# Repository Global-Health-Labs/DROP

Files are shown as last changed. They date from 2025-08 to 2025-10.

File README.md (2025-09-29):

# DROP Project Overview
DROP is a comprehensive automated diagnostic assay development platform developed by Global Health Labs. It's designed to accelerate and optimize the development of diagnostic tests, specifically focusing on:

- Lateral Flow Assays (LFAs) - rapid diagnostic tests like pregnancy tests or COVID antigen tests
- Nucleic Acid Amplification Tests (NAATs) - molecular tests like PCR, LAMP, and RPA

# Development Benefits

- Accelerated Timelines: Reduces development time and hands-on work
- Improved Scalability: Enables large-scale experiments
- Enhanced Reproducibility: Minimizes human variability
- Cost Effective: Reduces resource requirements for assay optimization

# Key Components
1. Hardware Platform

- Built around a Hamilton STAR liquid handling robot
- Custom 3D-printed LFA strip and cassette holders
- Integrated camera system for automated imaging
- Specialized deck layouts for different assay types
- HEPA filtration and UV sterilization for NAAT applications

2. Software Ecosystem

**RADA (Robotic Assay Development Application)**

- AWS-based web application that simplifies robot operation
- Generates worklist files (CSV instructions for the robot)
- Features separate interfaces for LFA and NAAT experiments
- Includes admin capabilities for managing users, deck layouts, and liquid classes
- Built with user-friendly interface to reduce technical barriers

**Image Analysis Software**

- Python-based LFA image analysis tools (LFA_image_analysis)
- Automated analysis of test and control lines
- Signal-to-noise ratio calculations
- Flexible parameters for different LFA formats

**Supporting Tools**

- Robot worklist generators
- Thermocycler analysis software
- Documentation system (MkDocs-based)

3. Protocols and Methods

- Standardized workflows for both LFA and NAAT development
- Design of Experiments (DoE) approaches
- Validation procedures and troubleshooting guides

# Applications
The DROP system has been used for:

**LFA Applications:**

- Antibody pair screening and optimization
- Membrane material optimization
- Buffer condition optimization
- Conjugate chemistry development
- Drying and spraying condition optimization

**NAAT Applications:**

- PCR optimization
- LAMP (Loop-mediated Isothermal Amplification) development
- RPA (Recombinase Polymerase Amplification) optimization
- Primer design and validation

# Current State

- Complete hardware and software designs are available on GitHub
RADA web application is deployment-ready
- Comprehensive documentation and troubleshooting guides included
- Proven track record in accelerating diagnostic development

This is a sophisticated, production-ready platform for automated diagnostic assay development that combines robotics, custom software, and validated protocols to streamline the traditionally manual and time-intensive process of diagnostic test optimization.

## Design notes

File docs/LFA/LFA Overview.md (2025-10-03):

Lateral Flow Assays (LFAs) are a popular diagnostic technology that enables sophisticated protein based chemistries to be run at or near the point of care. With low cost and ease of use, LFAs have been used for applications that span across a wide range of targets. These targets include bacteria, viruses, toxins, and more. Even though the use of these tests is fairly straightforward, there can be a significant investment required to create high performance LFAs. 

An example of a traditional LFA is shown in Figure 1 below. This is an example of a direct immunoassay, where a capture antibody is immobilized on the test membrane that is specific to the analyte of interest. A control antibody is immobilized on a second line to verify that the test results can be interpreted correctly. Antibodies conjugated to a label, often a gold or latex nanoparticle, are dried into a conjugate pad placed upstream from the test membrane. Before the conjugate pad, a sample pad is placed onto which the sample and/or running buffers are placed when the LFA is run. Downstream from the test membrane is a wicking pad, which helps to drive fluid flow through the test membrane. 

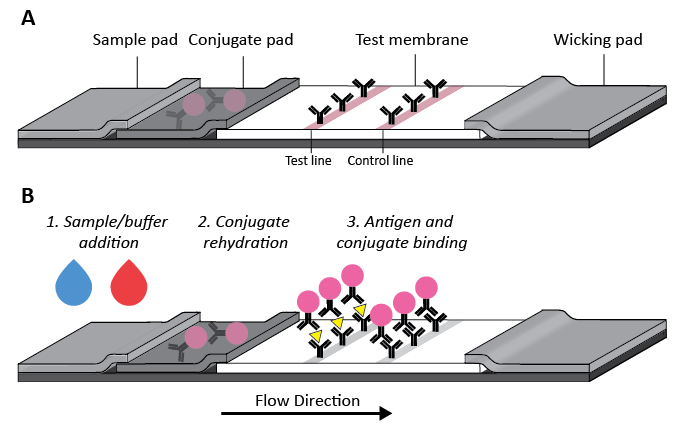
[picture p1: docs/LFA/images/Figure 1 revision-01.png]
LFA Background
 <br>
<small>Figure 1. Schematic of a classic LFA, from https://doi.org/10.1007/s00216-022-03897-9. The image depicts the materials involved in an LFA, which often includes a sample pad, a conjugate pad, a test membrane onto which a test and control ine are striped, and a wicking pad to drive flow (A). Typical use involves the addition of a sample and/or buffer to the sample pad, which flows downstream to rehydrate the conjugate dried into the conjugate pad (B). Liquid then moves into the test membrane onto which a test and/or control line will appear depending on whether analyte is present in the sample. All remaining liquid and unbound proteins then flow into the wicking pad. </small>

While an LFA is designed to be an quick and easy to use diagnostic, there are a lot of components that go into the optimization process. This includes, but is not limited to: 

1. Materials choice and dimensions: sample pad, conjugate pad, test membrane, wicking pad, and backing card
2. Material treatment: blocking, prewetting, etc
3. Assay format: direct, competitive, streptavidin test line with biotinylated capture antibody, etc
4. Molecular recognition element(s): antibody or antibody fragment, aptamer, proteins generated through directed evolution, computational, or rational design
5. Conjugation chemistries
6. Striping, spraying, and drying conditions 
7. Running buffer components 
8. Assay timing 

To address the time and monetary cost involved in LFA research and development, GH Labs developed a platform utilizing an automated liquid handling system. This system, termed RoboLFA, is a subcategory of the DROP platform. RoboLFA consists of LFA specific hardware, software, and protocols to enable large optimization or characterization expriments with limited hands-on time required. The system is described in detail in a paper by Anderson et al<sup>[1](https://link.springer.com/article/10.1007/s00216-022-03897-9)</sup>. Two applications using the roboLFA system are discussed in papers by Cate et al<sup>[2](https://pubs.acs.org/doi/10.1021/acsomega.1c01253)</sup> and Cantera et al<sup>[3](https://pmc.ncbi.nlm.nih.gov/articles/PMC8340086/)</sup>. Additional information on how to implement and/or modify this system is found in the respective sections for Hardware, Software, Protocols, and Example Efforts. 

## References
<small>
[1] Anderson, C.E., Huynh, T., Gasperino, D.J. et al. Automated liquid handling robot for rapid lateral flow assay development. Anal Bioanal Chem 414, 2607–2618 (2022). https://doi.org/10.1007/s00216-022-03897-9 <br>
[2] Cate, D. M., Bishop, J. D., Hsieh, H. V., et al. Antibody Screening Results for Anti-Nucleocapsid Antibodies Toward the Development of a Lateral Flow Assay to Detect SARS-CoV-2 Nucleocapsid Protein. ACS Omega 2021 6 (39), 25116-25123. DOI: 10.1021/acsomega.1c01253 <br> 
[3] Cantera, J. L., Cate, D. M., Golden, A., et al. Screening Antibodies Raised against the Spike Glycoprotein of SARS-CoV-2 to Support the Development of Rapid Antigen Assays. ACS Omega 2021 6 (31), 20139-20148. DOI: 10.1021/acsomega.1c01321 <br> </small>

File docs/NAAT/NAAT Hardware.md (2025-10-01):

Custom hardware is not required to run NAAT assays, as the Hamilton STAR system is already equipped to handle both tube- and plate-based workflows. For enhanced flexibility, we’ve included CAD files below that allow for the modification of commercially available cooling blocks to accommodate 0.5–2 mL tubes. These modified blocks are compatible with the Hamilton cooling deck, enabling efficient temperature control without the need for proprietary components.

:simple-opensourcehardware: - [CAD Files](https://github.com/Global-Health-Labs/DROP/tree/main/hw)

**Table 1.** Modifications to heating/cooling blocks to enable alignment on cooling deck. 

| No.| File Name       | Description    | Vendor            | Part No. | Qty  | Modified | Link  |
| :--| :-------------- | :------------- | :---------------- | :------- | :--: |:-------- |:-----: |
| 1  | 047295.SLDPRT  | 2 mL tube holder block| NA        | NA      | 1    |Holes for alignment posts| Hamilton #188035|
| 2  | 047296.SLDPRT  | 0.5 mL tube holder block | NA     | NA      | 1    |Holes for alignment posts| Hamilton #188035|

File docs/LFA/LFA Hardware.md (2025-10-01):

LFAs can come in many different forms. We have developed holders to address two of the most commonly used formats, a strip and a cassette. Other form factors can be integrated, but may require additional development to get a holder that is compatible with both the form factor of the LFA and the form factor of the deck postiions on the Hamilton STAR. These holders may also be adapted to other liquid handling systems. 

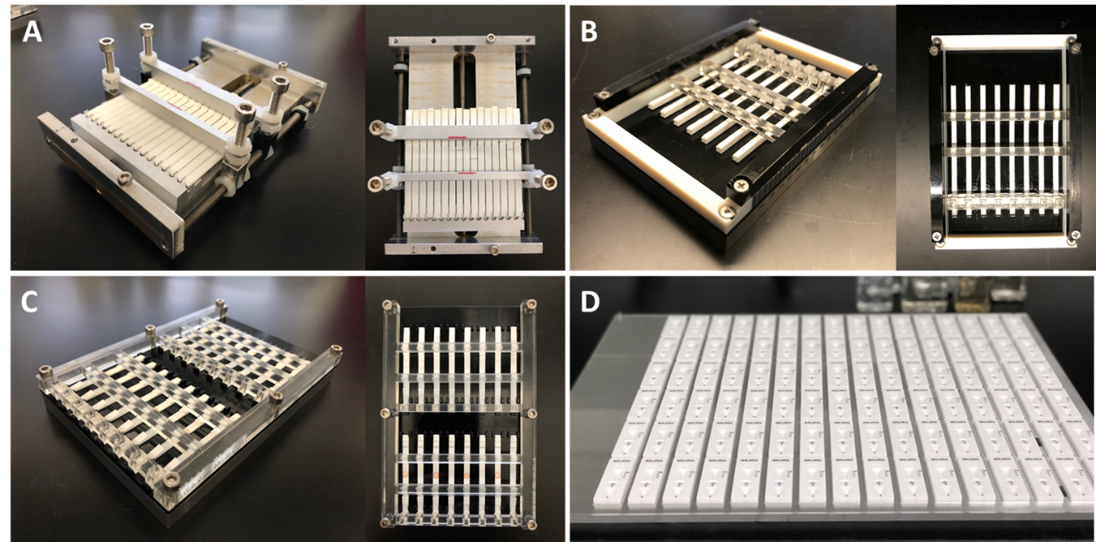
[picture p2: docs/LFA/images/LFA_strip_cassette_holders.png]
LFA Strip Holders
 <br>
<small>Figure 1. Image of the developed LFA strip (A), (B), and (C), and cassettes (D) from https://doi.org/10.1007/s00216-022-03897-9</small>

The objective of this document is to describe the pieces of hardware that might be required to operate the DROP system. This includes modifications to the base assembly from Hamilton, machined aluminum trays, laser cut acrylic sheets and 3D printed strip holders. This document has been prepared such that the entire assembly can be understood, as many parts relate to one another in the final deck layout.  

:simple-opensourcehardware: - [CAD Files](https://github.com/Global-Health-Labs/DROP/tree/main/hw)

### Custom Deck Modifications

The CAD files required for the custom deck modifications are broken into individual assemblies. These modifications assume that the carrier is an older version of the Hamilton Carrier. Newer version of the Hamilton Carrier are plastic and have slightly different dimensions. Additional development to add the alignment posts would be required if using a newer Hamilton Carrier for LFA applications. 

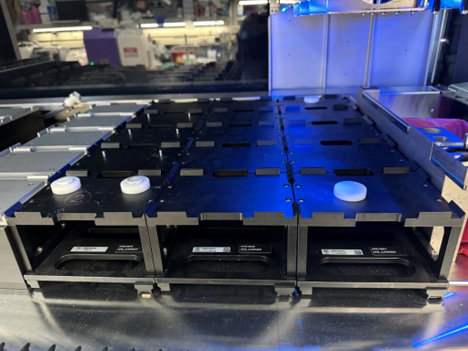
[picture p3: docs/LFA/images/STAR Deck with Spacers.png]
Hamilton Deck Modifications
 <br>
<small>Figure 2. Hamilton base carriers that have pegs and spacers added in their desired locations.  Associated parts are described in Tables 1 and 2.</small>

**Table 1.** Assembly of Hamilton base carriers that are modified so they can provide fiducial markers when LFA or cassette holders are placed on top. 

| No.| File Name       | Description    | Vendor             | Qty   | Modified | Link |
| :- | :-------------- | :------------- | :----------------  | :--: |:-------- |:---: |
| 1  | 047284.SLDASM   | Base assembly  | Hamilton Robotics  | 3     |          |      |
| 2  | 047283.SLDPRT   | Carrier base   | Hamilton Robotics 188039/00 | 1     |          | 1    |
| 3  | 047279.SLDASM   | Hamilton stand | Hamilton Robotics  | 3     |          | 1    |
| 4  | 047274.SLDPRT   | Top plate      | Hamilton Robotics  | 3     | Pin holes added | 3 |
| 5  | 047275.SLDPRT   | Leg            | Hamilton Robotics  | 2     | No       | 3    |
| 6  | 047281.SLDASM   | Hamilton stand | Hamilton Robotics  | 1     |          | 1    |
| 7  | 047273.SLDPRT   | Top plate      | Hamilton Robotics  | 1     | Pin and threaded holes added| 6 |
| 8  | 047275.SLDPRT   | Leg            | Hamilton Robotics  | 2     | No       | 6    |
| 9  | 047282.SLDASM   | Hamilton stand | Hamilton Robotics  | 1     | No       | 1    |
| 10 | 047277.SLDPRT   | Top plate      | Hamilton Robotics  | 1     | No       | 9    |

**Table 2.** Alignment posts and spacers to enable correct assembly. 

| No.| File Name       | Description    | Vendor            | Qty  | Modified | Link  |
| :- | :-------------- | :------------- | :---------------- | :--: |:-------- |:-----: |
| 11 | 047288.SLDPRT   | Alignment posts| Custom            | 2    |          | 1 + 16 |
| 12 | Hamilton_spacer.SLDPRT | Spacer with top hat | Custom| 2    |          | 1 + 16 |
| 13 | Hamilton_spacer_2.SLDPRT | Flat spacer | Custom        | 2    |          | 1 + 16 |

Note: Hamilton_spacer.SLDPRT doesn’t correctly account for tolerances, there is a need for us to improve the file to account for tolerances if this part is 3D printed.

### RoboLFA Strip Holder 
An LFA strip holder is helpful when a cassette has not yet been designed or the LFA dimensions are still requiring adjustment. Some LFAs on the market are in strip form, such as *Milenia Biotec HybriDetect Universal Lateral Flow Assays* and over-the-counter HCG tests, and therefore would stay in this category throught the entire research and development lifecycle. On this site we will mostly discuss our most commonly used strip holder, which consists of the following:

- Aluminium plate (85.5 x 127.8 mm) with six holes compatible with (#6-32) screws  
- 3D printed base plate designed to fit the width and length of the LFA strips
- 3D printed top plate designed with necessary pinch points, wells for reagent addition, and read window   
- 6 Screws (6/32 x 1/2")

When starting a new RoboLFA effort, it is critical to understand the requirements for a strip holder. This includes the length and width of the strip, the location and thickness of pinch points, the location and volume required for reagent addition, and the location and size of the read window. Each of these factors can be modified in the CAD files linked below. More detailed instructions can be found [here](./LFA%20Protocols.md). 

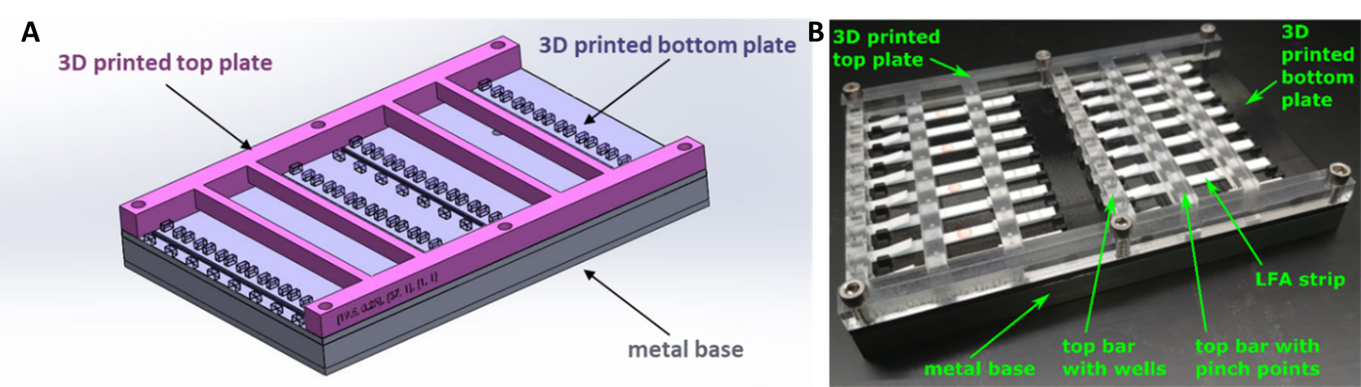
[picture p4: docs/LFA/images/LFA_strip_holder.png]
LFA Strip Holders
 <br>
<small>Figure 2. Strip holder to hold non-cassetted LFAs. The designed holder consists of three parts, (1) an aluminum base plate, (2) 3D brinted base plate and (3) 3D printed top plate. The bottom plate is designed with guide posts for consistent placement of a strip, while the top plate is designed to have pinch points and wells where required. Image from https://doi.org/10.1007/s00216-022-03897-9</small>

**Table 3.** LFA Strip Holder which consist of an aluminum base onto which 3D printed pieces are screwed. Similar to the RoboLFA Cassette Holder, The size and spacing of the strips can be varied depending on the need of the specific LFA. The dimensions of the wells, pinch points, and read windows can all be modified as needed. We typically have used ABS (acrylonitrile butadiene styrene) for this part.

| No.| File Name       | Description    | Vendor            | Qty  | Modified | Link  |
| :- | :-------------- | :------------- | :---------------- | :--: |:-------- |:-----: |
| 14 | 047286.SLDPRT   | LFA strip holder base | Custom            | 1-5  |          | 1 |
| 15 | 056923.SLDPRT (LFA Holder 3)| LFA strip top+bottom frame|Custom| 1-5  |          | 14|

We have two other versions of the strip holder that have some usability issues that need to be addressed. The other two strip holders are either challenging to set up reproducibly or require additional engineering on the clamping mechanism. More details about both of these holders can be found in the [supplemental material](https://doi.org/10.1007/s00216-022-03897-9). 
If we were to get additional time to further improve the strip holders, the most promising holder is the lego inspired assembly that allows for different 3D printed cross bars to be added interchangeably in 0.5mm increments along the length of the holder. This design allows for the manual adjustment of holder components (wells, pinch points, etc) without the need to manufacture additional parts.

### RoboLFA Cassette Holder
An LFA cassette holder is used when the strip dimensions have been locked and is further along the R&D pipeline. The cassette holder has defined spacing, allowing for precise liquid delivery and imaging across a large number of LFA devices.  

The cassette holder consists of:  

+ A 1/4" aluminum plate (40 x 48 cm) with the following modifications  
    - Two pins to guide the acrylic sheet in place  
    - Two drilled holes (dimensions) that enable consistent placement of the cassette holder onto the Hamilton Deck  
+ A 1/16" acrylic sheet (40 x 48 cm) with the following modifications
    - Laser cut to fit the cassette dimensions (example CAD files fit 80 and 96 cassettes respectively)
    - Two pin holes to guide on the aluminum plate 

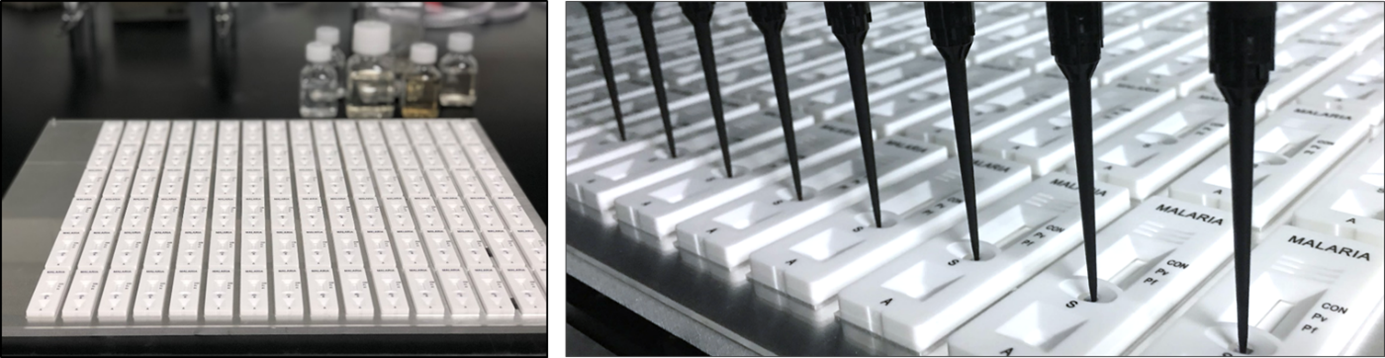
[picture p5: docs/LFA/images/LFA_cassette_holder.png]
LFA Cassette Holders
 <br>
<small>Figure 3. Holder for cassetted LFAs. The designed holder consists of two parts, (1) an aluminum base plate, (2) a laser cut 1/16" acrylic sheet designed to fit cassettes with little "wiggle room".  Image from https://doi.org/10.1007/s00216-022-03897-9</small>

| No.| File Name       | Description    | Vendor             | Qty  | Modified | Link  |
| :- | :-------------- | :------------- | :---------------- | :--: |:-------- |:-----: |
| 16 | 047287.SLDPRT   | LFA cassette deck| Custom            | 1    |Holes for alignment posts and posts for cassette holder| 12 + 13 |
| 17 | 038379_v1.SLDPRT or  038379_v2.SLDPRT (LFA Holder 4) | LFA cassette holder | Custom            | 1    |Holes for posts and cassettes (LFA cassette dependent)| 16 |

## Deck build 

The hardware above is placed onto the deck in the following, respective manners, for the cassette and strip holders. 

Deck Layout with cassette holder <br>
<small>Figure 4. Deck layout with cassette holder and corresponding guidance spacers. </small>

Images of deck build with both the LFA strip holder 

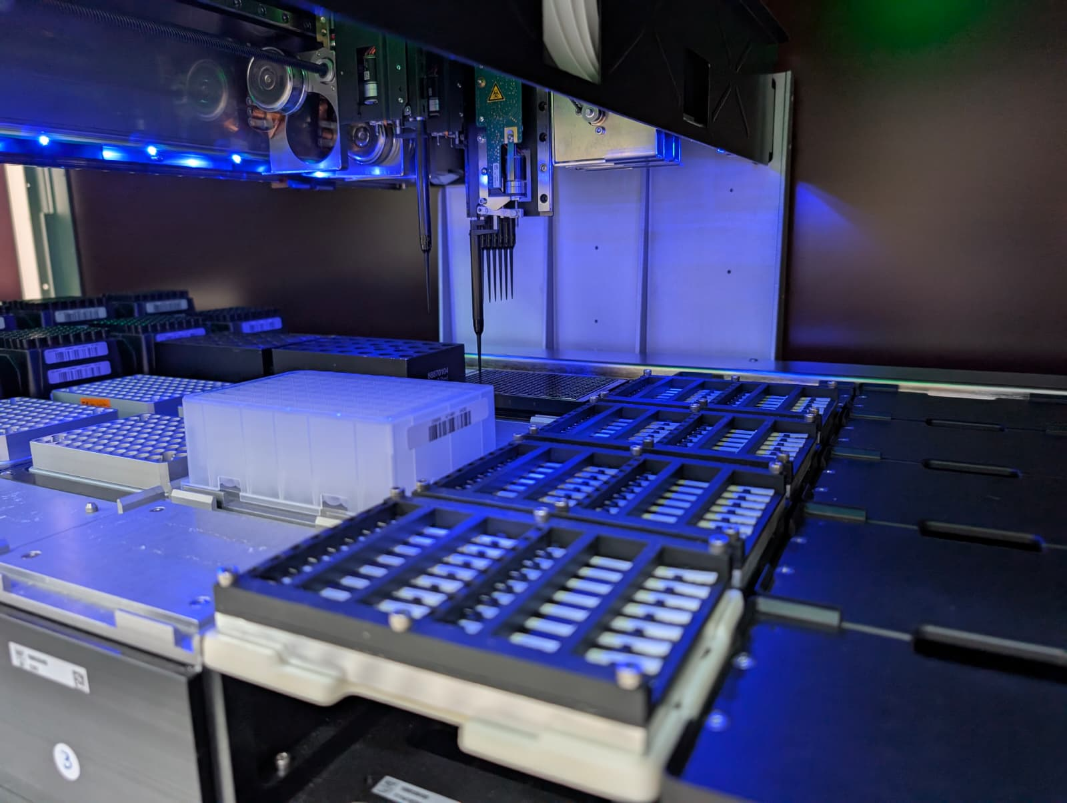
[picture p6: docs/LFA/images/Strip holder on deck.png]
Deck Layout with LFA strip holder
 <br>
<small>Figure 5. Deck layout with strip holder. </small>

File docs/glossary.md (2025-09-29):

## Definitions

There is a lot of jargon associated with the DROP system. The definitions are grouped into sections based on the time of need, including general use, working with worklists, etc. 

## Abbreviations
| Term             | Definition                          |
| :--------------- | :----------------------------------- |
| `NAAT`           | Nucleic Acid Amplification Test |
| `LFA`            | Lateral Flow Assay |
| `DROP`           | Diagostic Robotic Optimization Platform |
| `AWS`            | Amazon Web Services|
| `RADA`           | Robotic Assay Development Application |
| `RPA`            | Recombinase Polymerase Amplification |
| `LAMP`           | Loop-mediated Isothermal Amplification |
| `PCR`            | Polymerase Chain Reaction |
| `DW`             | Deep well plates | 
| `NTR`            | Nesting tip racks | 
| `RDT`            | Rapid diagnsotic test |

## General definitions 
| Term                     | Definition                          |
| :----------------------- | :----------------------------------- |
| `worklist`        | The worklist is a .csv file that is input into the Hamilton Run Control to the robot what actions to follow and in what order. The file containing the worklist must end with ‘worklist.csv’ otherwise the Hamilton software will not recognize it. The file containing the worklist must end with worklist.csv; otherwise, the Hamilton software will not recognize it. The file must be a plain .csv file (not a UTF-8 or any other csv version). A worklist can be made manually or by coding. For LFA optimization work, we have python-based code called the “Robot Worklist Generator”. The worklist is composed of 21 columns (two of which are optional) and infinite rows. The identity and definition of each of these columns is described in Section 8. The order of the columns does not matter.  |
| `Method`          | A Hamilton specific piece of software that has been designed to carry out an experiment. Methods can be simple (always pipette a known volume between known locations) or complex (insert a .csv file with a range of different commands that can pipette any volume within reason between any location available on the deck). |
| `Deck`            | The area on the robot where things happen. It includes where the pipette tips are stored, where plates can be placed, and even includes the waste area. |
| `Stock plate(s)`  | Plates that have all stock reagents required for the experiment. Typically, we can use the stock plates as the location to prepare and mix the mastermix as well. |
| `Assay plate(s)`  | Plates where the mastermix and sample (or just template) are added. We have spots on the deck for both 96 well and 384 well PCR plates. A flat bottom plate can also be used as an "assay plate", depending on the application.|
| `Liquid Class(es)`| A liquid class is built to pipette a given liquid, and has information around aspiration speeds, dispense speeds, blowout volumes, air transports, etc and a calibration curve. We have liquid classes developed for a range of liquids, and more can be made as needed. This requires one of our LVK trained lab staff to assist. |

## Worklist column definitions 

| Term              | Definition                          |
| :---------------- | :----------------------------------- |
| `step`            | A text string to describe what the step is (e.g. conjugate addition, sample addition, buffer addition, imaging)|
| `volume_uL`       | Volume to be pipetted. Must be smaller than the volume associated with the liquid class (50, 300, or 1000 depending). If volume is set to 0, the robot will take a picture instead of pipetting.|
| `liquid_class`    | Liquid class associated with the liquid to be pipetted. These classes have been designed specifically for the liquids that we pipette and the volumes we plan to use. There is a list of possible liquid classes found in the CO-RE liquid editor. The specific liquid classes designed for LFAs can be found in the LFA documentation.|
| `tip_type`        | This value is associated with the liquid class selected and the volume to be pipetted. This value will be either 50, 300, or 1000. This value needs to be larger than the volume to be pipetted.|
| `dispense_type`   | Two dispense types, "Surface_Empty" and "Jet_Empty" are used. Surface_Empty goes to the tip of the liquid, detected using a capacitive measurement, and dispenses 2mm below that height. This feature struggles when there are bubbles at the top of a liquid. Jet_Empty goes inside the well and dispenses at a set height above the bottom of the well plate. Jet_Empty tends to be accurate at faster speeds than Surface Empty.|
| `asp_mixing`      | Programs the number of mixing cycles performed after a dispense step. This value needs to be the same value for an entire group. This feature only works for Surface_Empty liquid classes.|
| `source`          | The name of the liquid that is being pipetted. By using specific descriptors, source can be useful for the user when designing the worklist. |
| `group_number`    | The "group" classification is an important one. Each group needs to be from the same tip_type (50, 300, 1000). The group number is used by the robot to control the order and timing of pipetting steps. It is recommended to keep groups of 8 rows if you want to control the order in which the robot completes each step. Note: if one item in a group has mixing step, for example, then all items in that group will be mixed. However, using too many groups will make the method too slow. Therefore, group numbers need to be assigned wisely.|
| `timer_delta`     | If the assay has time dependent steps, a value to program a time delay between the step and the next (associated) step, defined in timer_group_check. The value here is in seconds.|
| `timer_group_check`| This value will tell the program which step from which the time should refer to, in seconds. For example, if you wanted group 3 to occur 10 minutes after group 1 is complete, then your group_number=3, timer_group_check=1, and timer_delta (for group 1) = 600.|
| `touchoff_dis`    | Used to change the distance vertically that the pipette tip moves up after touching a surface before dispensing.  Set value to -1 when not in use.|
| `to plate`        | The ID of the plate pipetting step is going to. For most cases, there are more than one of each type of plate on the deck, indicated by the number at the end of the to_plate ID. Plates used in LFA applications are the following: TABLE INSIDE TABLE? |
| `to_well`         | Where pipetting step is going to. The ID ranges from 1-96 for 96 well plates, and 1-384 for 384 well plates. Independent of plate size, the numbering is always top to bottom, left to right. Examples of the layout for each plate type are shown below.|
| `from_plate`      | Plate ID where pipetting step is coming from. See to_plate above for more information about plate IDs. |
| `from_well`       | Well ID where pipetting step is coming from. See to_well above to see more information about well IDs.|
| `step_index`      | This does not matter. Set value to 0. |
| `destination`     | This value can be used to name the destination location, which can be useful when making the worklist. Not required by Hamilton software and can be set to default value of 0 if desired.|
| `guid`            | ID number associated with that specific well or LFA. guid is used for tracking when multiple steps are associated with one assay or assay type.|
| `from_path`       | String value used to track events. Currently not integrated into workflow. Recommend setting to default value, which is “some path” and use other columns to do so instead.|
| `dx`            | Denotes pipetting location in the x-axis. Origin (0,0) coordinates are hardware dependent, but generally located in the bottom left side of the geometry. Need to be manually verified prior to use.|
| `dz`            | Denotes pipetting location in the z-direction. This value is hardware and instrument dependent. Needs to be manually verified prior to use.|

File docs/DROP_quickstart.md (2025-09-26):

## :material-robot-outline:  **Step 0: Equipment set up**

DROP is an add on to a Hamilton STAR system that consists of hardware, software, and protocols specific to this work. Other Hamilton systems could be used with some modifications to the Method/Layout files and LFA hardware. 

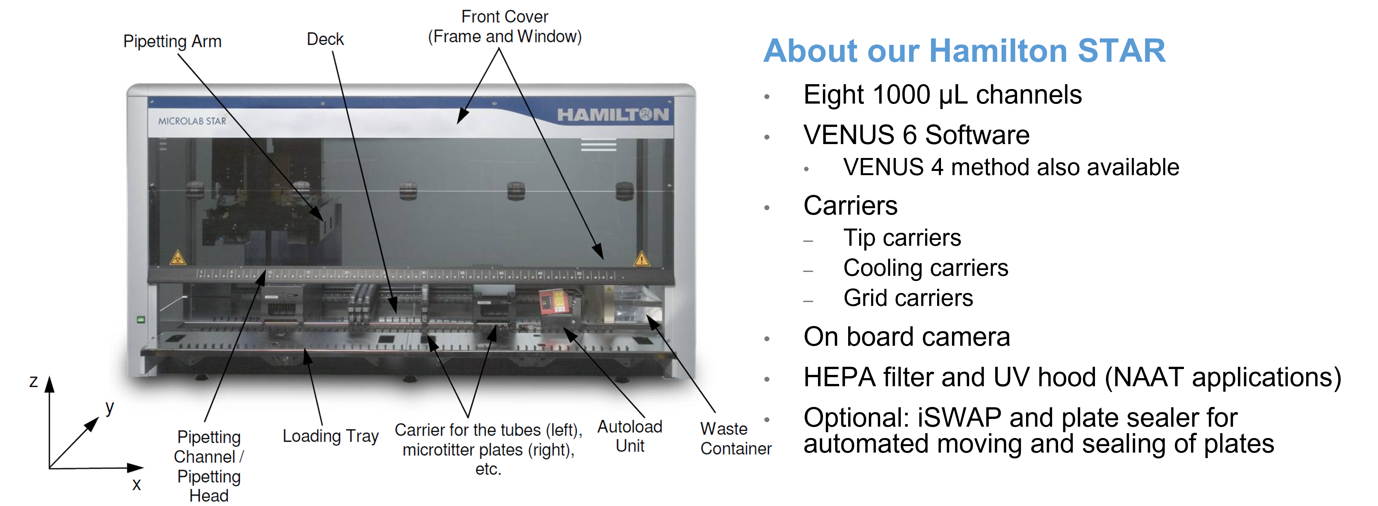
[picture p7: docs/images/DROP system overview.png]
DROP STAR
 <br> <br>
<small>Figure 1. Image of Hamilton STAR with specific add ons required for DROP. This includes 8 individual pipetting channels (other options are 96 and 384 head, which work well for plate applications but are not flexible enough for LFA applications), VENUS software, tip and plate carriers, and on board camera. NAAT applications also require a HEPA filter and UV light to reduce the risk of contamination. </small>

**Additional recommended capabilities:**

*LFA applications -*

+ Lateral flow strip preparation and assembly 
+ 3D printing (internal or outsourced) to make LFA strip holders 
+ Laser cutting (internal or outsourced) to make LFA cassette holders 

*NAAT applications -*

+ PCR hood for clean reagent preparation 
+ Gel capabilities 
+ Thermocyclers 

After setting up the Hamilton STAR and ancillary equipment, the software specific to the DROP system must be installed. More detail instructions for installation can be found under "DROP Installation". 

## :simple-materialdesignicons: **Step 1: Experimental Design**

Experimental design for LFAs and NAATs can take many forms. One of the major benefits of an automated liquid handling system is the ability to run large experiments with high reproducibility. Therefore, Design of Experiments (DoE) has been used as an approach to characterize and/or optimize different diagnostic chemistries in the most efficient and informative way possible. Some of our favorite approaches for DoE are:

+ Full factorial design to determine the best antibody pairs for a given antigen target 
+ Taguchi design for PCR optimization 

More detail on each of these can be found in the respective RoboLFA and RoboNAAT Modules. 

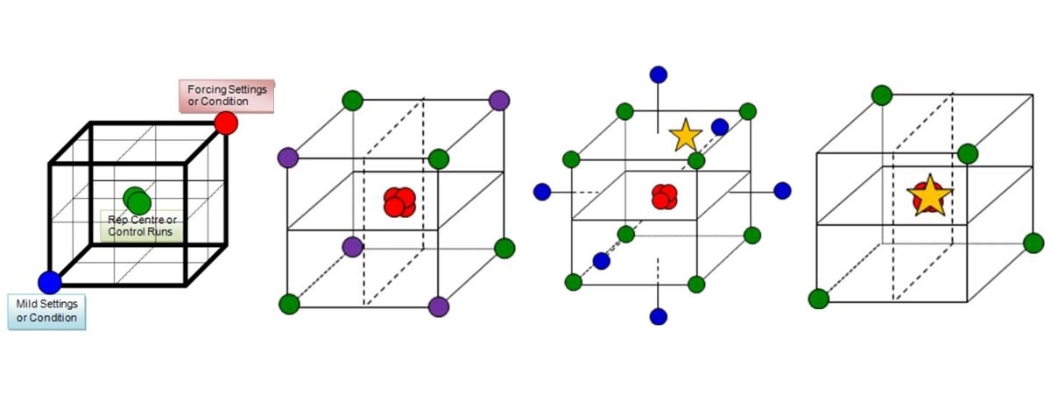
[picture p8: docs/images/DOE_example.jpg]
DROP DOE
 <br>
<small>Figure 2. Graphical representation of experimental designs for a 3-dimensional experimental space. Image from [Prism UK](https://prismtc.co.uk/resources/blogs-and-articles/the-sequential-nature-of-classical-design-of-experiments).  </small>

## :material-test-tube: **Step 2: Experiment Setup**

Experiment setup includes preparation of the required materials to run the experiment as well as the worklist. 

+ For LFA experiments, this can include making antibody conjugates and preparing LFA membranes
+ For NAAT experiments, this can include primer design and identification of the appropriate reagents and controls 

With this information, as well as the inputs from the Experimental Design step, a worklist with the step by step commands for the robot can be made. There are a few different ways to make a worklist, but we will mostly discuss the use of an AWS Web Application termed the Robotic Assay Development Application (RADA) designed for an improved user experience. 

## :material-hazard-lights: **Step 3: Experiment Validation**

Validation of a given experiment or protocol is even more important when working with an automated liquid handling system. Not only are there more things that can go wrong, but the potential impact of an error is much higher when operating with much larger experiments. For the DROP system, experiment validation includes:

+ Testing the worklist in simulation to identify errors on the software/robotics side
+ Testing the experiment with a subset of the final conditions to identify error modes that may impact outcome 

A full experiment should not be run if there are errors that occur in either of these two categories. 

## :material-robot-industrial: **Step 4: Run Experiment**

This step is exactly what it sounds like, run the experiment that has been designed and validated. Something to be mindful of is that there are efforts on the DROP system that can span multiple robot runs. 

## :octicons-graph-16: **Step 5: Data Analysis**

The DROP system includes two data analysis tools, one designed for analyzing LFA images captured using the Hamilton STAR and one for analyzing raw NAAT data from a thermocycler. Both tools utilize Jupyter Notebook and Python. More information about each tool can be found in their respective platform tabs (roboLFA and roboNAAT). 

## :material-repeat: **Step 6: Iterate**

As needed.

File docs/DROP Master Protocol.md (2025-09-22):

The DROP workflow (diagrammed in Figure 1 below) includes experimental design, experiment setup, experiment validation, running the experiment, and data analysis. This document specifically covers the procedures for Steps 3 and 4: experiment validation and running the experiment. Additional information about assay specific experimental design, setup, and data analysis can be found in their respective pages under RoboNAAT and RoboLFA. 

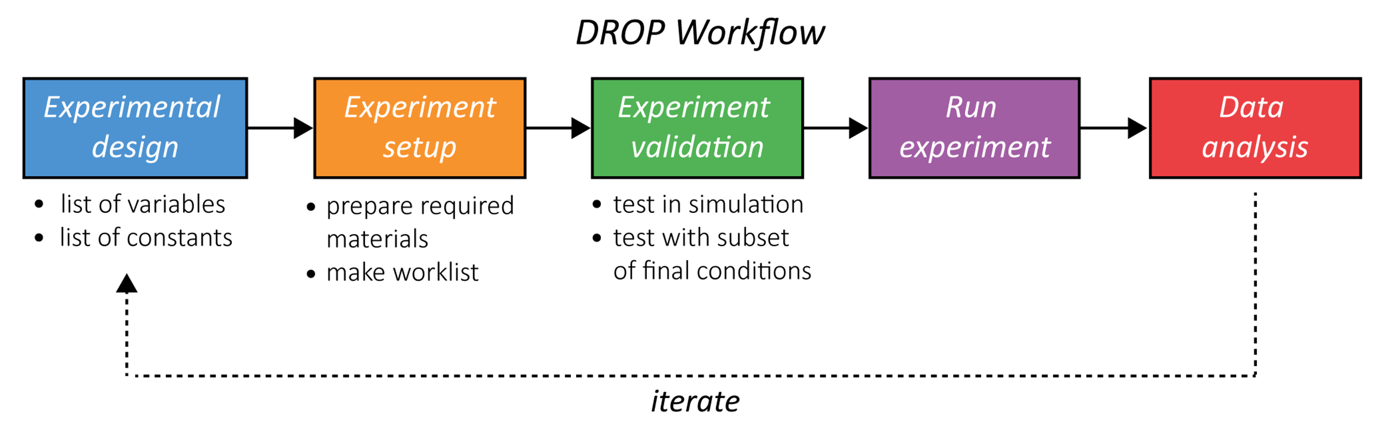
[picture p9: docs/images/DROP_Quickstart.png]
DROP Quickstart
 <br>
<small>Figure 1. High level overview of the DROP workflow. This workflow includes (1) Experimental design (2) Experiment setup (3) Experiment validation (4) Running an experiment and (5) Data analysis. In most applications, futher iteration would continue until product criteria are met.  </small>

### Experiment preparation 

Before running an experiment, it is recommended to complete the Daily Maintenence provided with the Hamilton system. Launch the Instrument Maintenence Program and follow the step by step instructions provided. 

NAAT applications are highly sensitive to contamination, therefore it is recommended to UV treat the hood for a minimum of 10 minutes before working with a potentially sensitive molecular assay. 

### Experiment confirmation 

1. Launch VENUS software 
2. Run Worklist in simulation mode 

!!! note 
    A worklist is generated using the Robotic Assay Development Application (RADA) or through manual methods. An explanation on how to make a worklist using either method can be found in the RADA tab. 
    
    All worklists must first be run in simulation mode to identify any potential problems before running the actual experiment. Use simulation mode to do the following: 
    •	Verify run by watching the deck layout.
    •	Optional: verify run using the trace file.
    •	Optional and recommended: add animation in the method. The animation provides realistic virtual x, y, z visualization.

## :material-robot-outline:  **Step 0: Equipment set up**

DROP is an add on to a Hamilton STAR system that consists of hardware, software, and protocols specific to this work. Other Hamilton systems could be used with some modifications to the Method/Layout files and LFA hardware. 

DROP STAR <br> <br>
<small>Figure 2. Image of Hamilton STAR, base of the DROP system, with specific add ons required for the build. This includes type of pipette head (other options are 96 and 384 head, which work well for plate applications but are not flexible enough for LFA applications), VENUS software, tip and plate carriers, and on board camera. NAAT applications also require a HEPA filter and UV hood to reduce the risk of contamination. </small>

**Additional capabilities recommended:**

*LFA applications -*

+ Lateral flow assay preparation and assembly 
+ 3D printing (internal or outsourced) to make LFA strip holders 
+ Laser cutting (internal or outsourced) to make LFA cassette holders 

*NAAT applications -*

+ PCR hood for clean reagent preparation 
+ Gel capabilities 

After setting up the equipment described above, the software specific to the DROP system must be installed. More detail instructions for installation can be found under "DROP Installation". 

## :simple-materialdesignicons: **Step 1: Experimental Design**

Experimental design for LFAs and NAATs can take many forms. One of the major benefits of an automated liquid handling system is the ability to run large experiments with high reproducibility. Therefore, Design of Experiments (DoE) has been used as an approach to characterize and/or optimize different diagnostic chemistries in the most efficient and informative way possible. Some of our favorite approaches for DoE are:

+ Full factorial design to determine the best antibody pairs for a given antigen target 
+ Taguchi design for PCR optimization 

More detail on each of these can be found in the respective roboLFA and roboNAAT Modules. 

DROP DOE <br>
<small>Figure 3. Graphical representation of experimental designs for a 3-dimensional experimental space. Image from [Prism UK](https://prismtc.co.uk/resources/blogs-and-articles/the-sequential-nature-of-classical-design-of-experiments).  </small>

## :material-test-tube: **Step 2: Experiment Setup**

Experiment setup includes preparation of the required materials to run the experiment as well as the worklist. 

+ For LFA experiments, this can include making antibody conjugates and preparing LFA membranes
+ For NAAT experiments, this can include primer design and identification of the appropriate reagents and controls 

With this information, as well as the inputs from the Experimental Design step, a worklist with the step by step commands for the robot can be made. There are a few different ways to make a worklist, but we will mostly discuss the use of an AWS Web Application termed the Robotic Assay Development Application (RADA) designed for an improved user experience. 

## :material-hazard-lights: **Step 3: Experiment Validation**

Validation of a given experiment or protocol is even more important when working with an automated liquid handling system. Not only are there more things that can go wrong, but the potential impact of an error is much higher when operating with much larger experiments. For the DROP system, experiment validation includes:

+ Testing the worklist in simulation to identify errors on the software/robotics side
+ Testing the experiment with a subset of the final conditions to identify error modes that may impact outcome 

A full experiment should not be run if there are errors that occur in either of these two categories. 

## :material-robot-industrial: **Step 4: Run Experiment**

This step is exactly what it sounds like, run the experiment that has been designed and validated. Something to be mindful of is that there are efforts on the DROP system can span multiple robot runs. 

## :octicons-graph-16: **Step 5: Data Analysis**

Included in the DROP system are two data analysis tools, one for analyzing LFA images taken on the Hamilton STAR and one for analyzing raw NAAT data from a thermocycler. Both tools utilize Jupyter Notebook and Python. More information about each tool can be found in their respective platform tabs (roboLFA and roboNAAT). 

## :material-repeat: **Step 6: Iterate**

As needed.

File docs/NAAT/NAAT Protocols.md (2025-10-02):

The DROP workflow, diagrammed in Figure 1 below, includes experimental design, experiment setup, experiment validation, running the experiment, and data analysis. This document specifically covers the procedures for Steps 3 and 4: experiment validation and running the experiment. Additional information about assay specific worklist generation and data analysis can be found in their respective pages. 

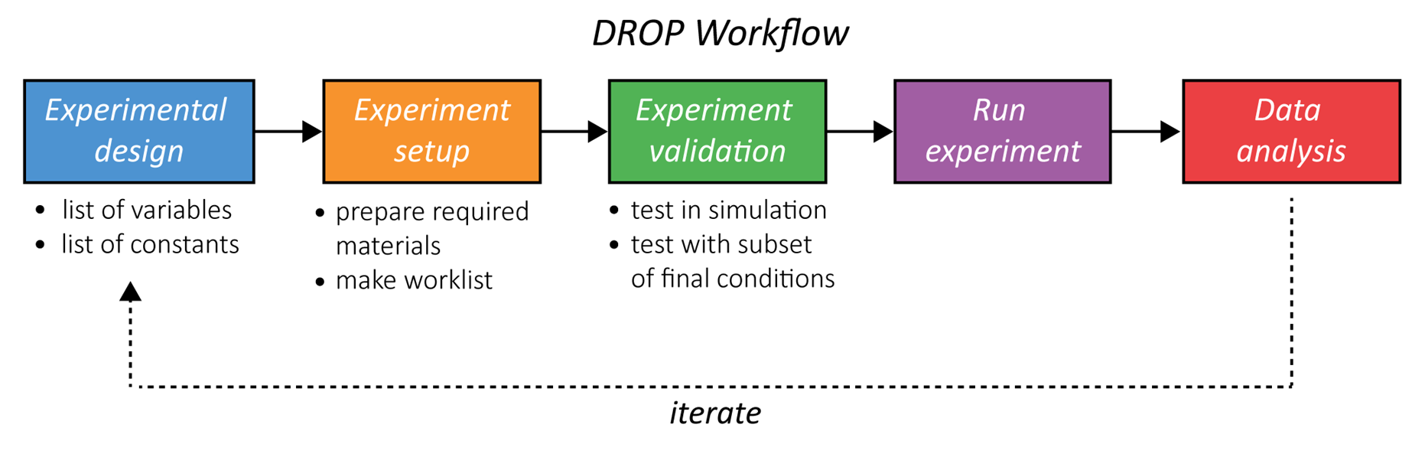
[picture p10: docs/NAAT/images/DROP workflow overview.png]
DROP Quickstart
 <br>
<small>Figure 1. High level overview of the DROP workflow. This workflow includes (1) Experimental design (2) Experiment setup (3) Experiment validation (4) Running an experiment and (5) Data analysis. In most applications, futher iteration would continue until product criteria are met.  </small>

## :octicons-checklist-16: **Experiment Checklist**

***A. Preparing for the experiment:***  

1. Design experimental protocol  
2. Define or specify any additional liquid classes, labware or hardware definitions needed
3. Source all necessary reagents, pipette tips, devices and plates  
4. Generate worklist    
5. Validate worklist in simulation   
6. Make modifications to worklist based on simulation results, as needed  
*Note plate locations and number of tips used*

***B. Running the experiment:***  

1. Prepare instrument deck   
2. Start refrigerated circulator (if required)  
3. UV treat and/or spray down deck with cleaning solution  
4. Complete Daily Maintenance. Skip, if already completed for the day.  
5. Load all required tips onto instrument  
6. Load reagents into reagent plates in PCR hood   
7. Load all reagent and assay plates required to run experiment onto Hamilton STAR  
8. Run worklist(s) on Hamilton STAR   
9. Seal assay plate(s)  
10. Vortex briefly and spin down assay plate(s)  
11. Place assay plate(s) onto thermocycler, load corresponding protocol and run  

***C. Finalizing experiment:***  

1. Clean deck and dispose of materials appropriately  
2. Analyze data   
3. Repeat as needed   

## :simple-materialdesignicons: **Experimental design**

A NAAT effort on the DROP system begins with reagent preparation for the selected assay. Typically, this starts with the formulation of a master mix, which include buffers, enzymes, primers, probes, and dNTPs. This master mix is prepared, mixed, and aliquoted into an experiment plate using the Hamilton STAR system.

To initiate a RoboNAAT workflow, primers and probes specific to the target of interest are first designed. Next, appropriate samples are selected for assay optimization and testing. Finally, the experimental framework is defined by establishing the scope, controls, and key variables.

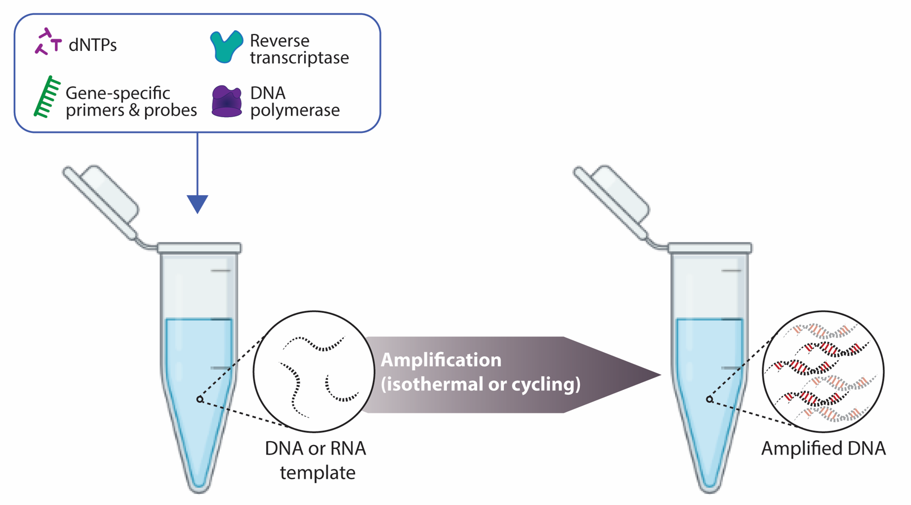
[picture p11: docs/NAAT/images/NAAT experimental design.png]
NAAT Experimental Design
 <br>
<small>Figure 2. Examples of variables that can be optimized using the RoboNAAT system. </small>

Design of experiment (DoE) describes an approach to systematically and efficiently study the effects of input variables on a process and its outputs [1]. This approach has been widely applied across disciplines, from traditional engineering applications to polymerase chain reaction. The precision and repeatability of an automated liquid handling robot like the Hamilton STAR significantly expands the possibilities for experimental design. 

Leveraging this capability, GH LAbs has explored DoE strategies, including the Taguchi Method and Definitive Screening Design, to optimize and develop assay and evaluate performance. When planning a RoboNAAT experiment, selecting an appropriate experimental design is critical to ensure sufficient statistical power for informed decision-making. There are a number of groups who have published on the use of Taguchi for PCR applications, two selected manuscripts are [Cobb et al 1994](https://pmc.ncbi.nlm.nih.gov/articles/PMC308365/) and [Celani de Souza et al 2011](https://pubmed.ncbi.nlm.nih.gov/21867748/). 

## :material-test-tube: **Experiment Setup**

Setup for a NAAT experiment involves the preparation of the working stock of all materials required to run the designed experiment. 

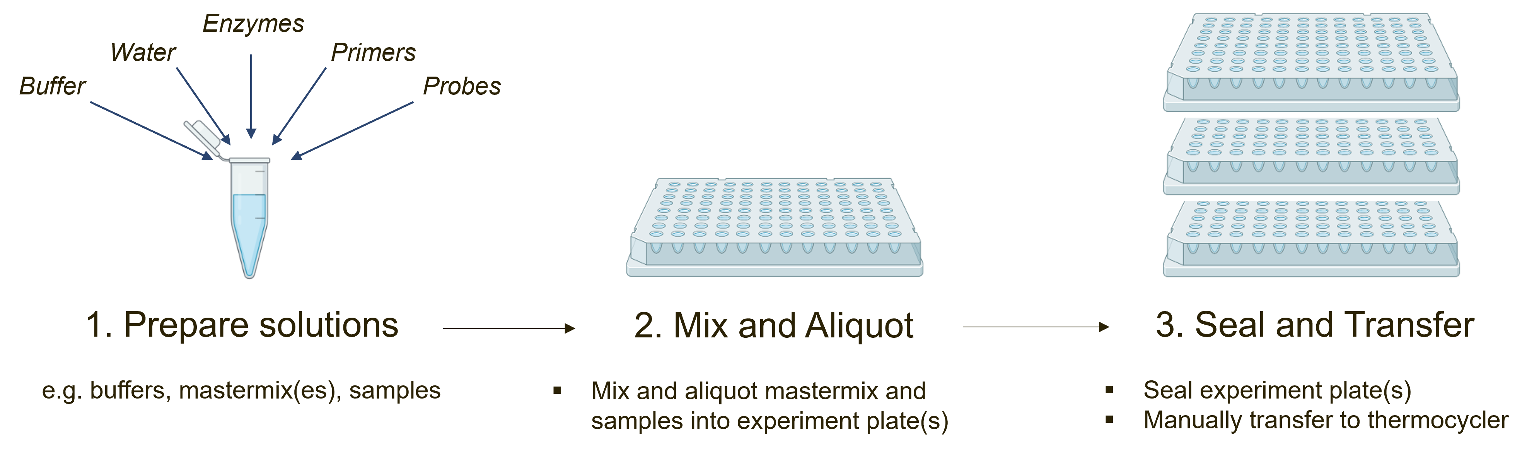
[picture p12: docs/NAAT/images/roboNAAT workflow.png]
NAAT workflow
 <br>
<small>Figure 3. Example workflow automated by RoboNAAT. </small>

### Adjusting hardware/labware

Most NAAT efforts use basic labware definitions, such as PCR plates, deep well plates, and tubes. These definitions come with the Hamilton software, and the only adjustments that are typically required are to dial in the labware locations in the Hamilton Layout file. 

### Optimizing liquid classes 

The DROP system has a comprehensive library of liquid classes designed to support a wide range of experimental workflows. Each liquid class is configured with precise pipetting parameters to ensure consistent and accurate liquid handling. Proper tuning of these parameters is critical for reliable performance, especially when working with diverse reagents in NAAT workflows.
Key parameters that can be adjusted include the flow rate, air transport volume, blowout volume, settling time, etc. 

Information on configuring and modifying liquid classes is available in the CO-RE Liquid Editor Help section. New liquid classes can be created and validated using the Hamilton Liquid Verification Kit (LVK). When a new liquid class is developed or an existing one is validated for a different reagent, it undergoes performance qualification to ensure it meets experimental requirements.
Below is a list of commonly used liquid classes for NAAT workflows on the DROP system.

| Liquid Class           | Tip size | Dispense Type     | Recommended validation for: |
| :-------------- | :-------------------- | :------------------- | :------------------- |
| RoboNAAT_tip50_buffer_SurfaceEmpty | 50|Surface Empty | Water, 10X Reaction buffers, 100mM magnesium |
| RoboNAAT_tip300_buffer_JetEmpty | 300|Jet Empty | Water, 10X IsoAmp buffers, 100mM magnesium |
| RoboNAAT_tip300_buffer_SurfaceEmpty | 300|Surface Empty | Water, 10X IsoAmp buffers, 100mM magnesium |
| RoboNAAT_tip50_primers_SurfaceEmpty | 50|Surface Empty | Primers, dNTPs, gDNA |
| RoboNAAT_tip300_primers_SurfaceEmpty | 300|Surface Empty | Primers, dNTPs, gDNA |
| RoboNAAT_tip50_enzymes_SurfaceEmpty | 50|Surface Empty | Any enzyme in 50% glycerol, other related viscous liquids |
| RoboNAAT_tip300_enzymes_SurfaceEmpty | 300|Surface Empty | Any enzyme in 50% glycerol, other related viscous liquids |
| RoboNAAT_tip1000_water_JetEmpty | 1000|Jet Empty | Water |
| RoboNAAT_tip1000_water_SurfaceEmpty | 1000|Surface Empty | Water |
| RoboNAAT_tip50_template_SurfaceEmpty | 50|Surface Empty | RNA or DNA template |
| RoboNAAT_tip50_organics_SurfaceEmpty | 50|Surface Empty | Ethanol |
| RoboNAAT_tip50_detergent_SurfaceEmpty | 50|Surface Empty | 5% Triton X-100, Tween-20, and PVP |
| RoboNAAT_tip50_buffer_JetEmpty | 50|Jet Empty | Aliquoting full mastermix |

!!! note
    Best practices recommend including the date and liquid class version in the validated liquid class documentation.

Once the above activities have been completed, the system is ready to run a NAAT experiment. An example checklist detailing the entire workflow can be found at the top of this page. 

### :material-microsoft-excel: **Generate worklist(s)**

Worklists can be generated using the Robotic Assay Development Application (RADA) or manually. Instructions for making a worklist using either method can be found in the RADA tab. 

## :material-hazard-lights: **Experiment Validation**

!!! note     
    All worklists must first be run in simulation mode to identify any potential problems before running the actual experiment. Simulation mode allows you to: 

    - Verify run by watching the deck layout.
    - Optional: verify run using the trace file.
    - Optional and recommended: enable animation in the method. The animation provides realistic virtual x, y, z visualization. Animation only applies when using VENUS 4. VENUS 6 does not currently have animation capabilities. 

1. To validate the worklist(s) generated for the experiment, first launch VENUS software 
2. Locate the relevant shortcut in either the “Frequently Used” section or the “Shortcuts” panel. Click the three dots on the right-hand side of the shortcut to open the menu. Select “Simulate Method” from the drop down. Once selected, Run Control will launch to execute the method in simulation mode. 

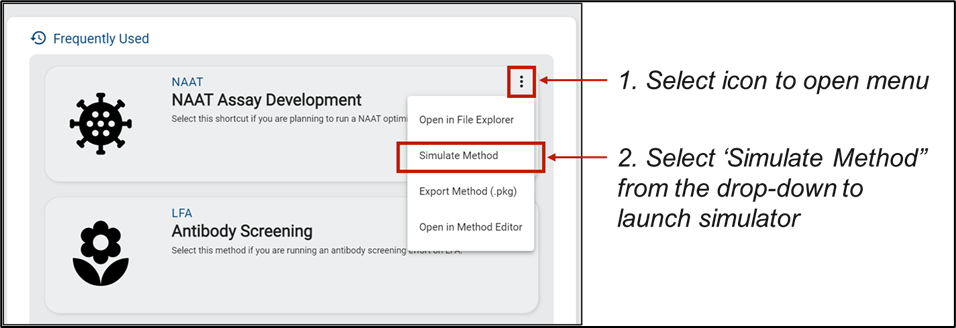
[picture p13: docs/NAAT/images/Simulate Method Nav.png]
Simulation Mode
     <br>
    <small>Figure 4. Navigation to enter Simulation Mode in VENUS 6 software. </small>

3. Confirm that the system is in simulation mode, this will be indicated in the upper-left corner of the window. Once confirmed, click the blue play button to begin simulation.

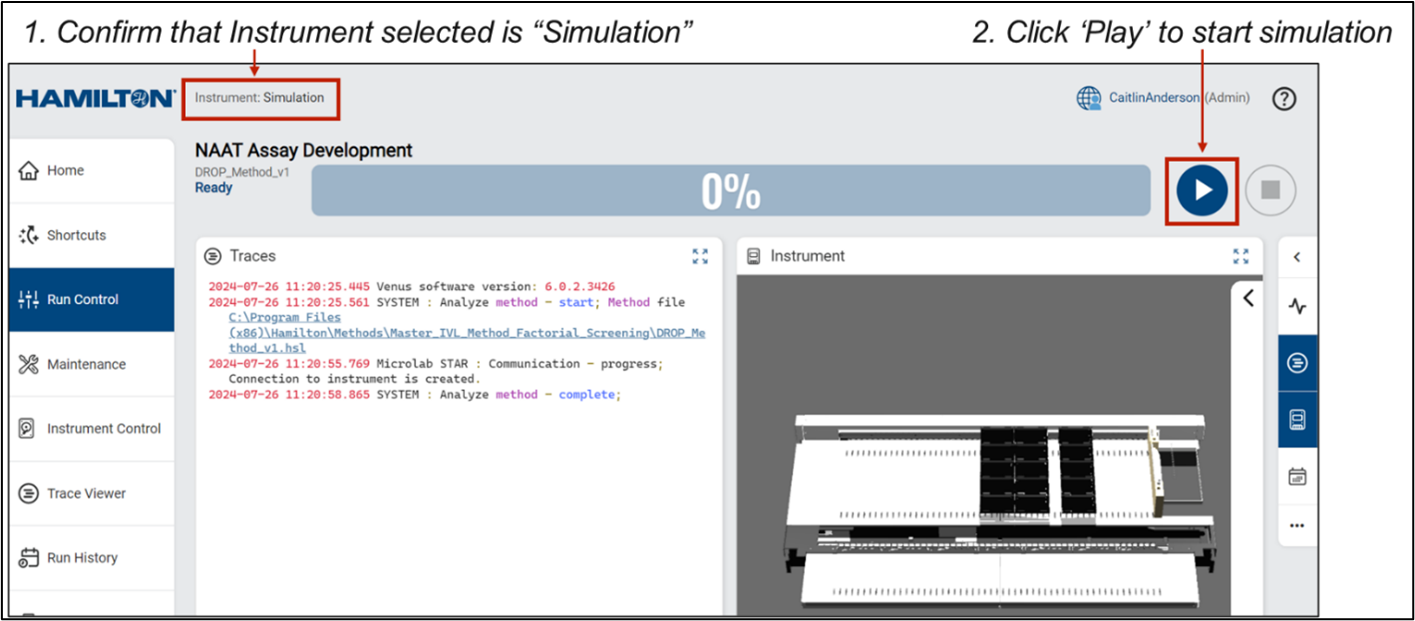
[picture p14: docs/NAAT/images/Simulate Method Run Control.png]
Simulate Method Run Control
     <br>
    <small>Figure 5. In Run Control, the mode can be viewed by noting the name listed next to “Instrument”.  In simulation mode, the programmed steps will not be sent to the machine itself. Instead they are sent to a virtual machine that simulates the entire method. In instrument mode, the programmed steps will be sent to the machine. All worklists should first be validated in simulation mode. </small>

4. Click the “…” button to browse and select the appropriate worklist file for the experiment. Once the file is loaded, the “Run” button will become active. Click “Run” to begin the simulation.
    
    !!! note 
        The worklist file must be a .csv file that ends with worklist.csv. If the file is of another type, the Hamilton software will not recognize it. 

        **Developer notes:** The Hamilton Method was developed in collaboration with the Hamilton Apps team. It inputs a *worklist.csv file where each row in the document corresponds to one robot step. The method file is intended to be flexible for a range of experimental designs. More information about this document, called a “worklist” can be found in the RADA tab.

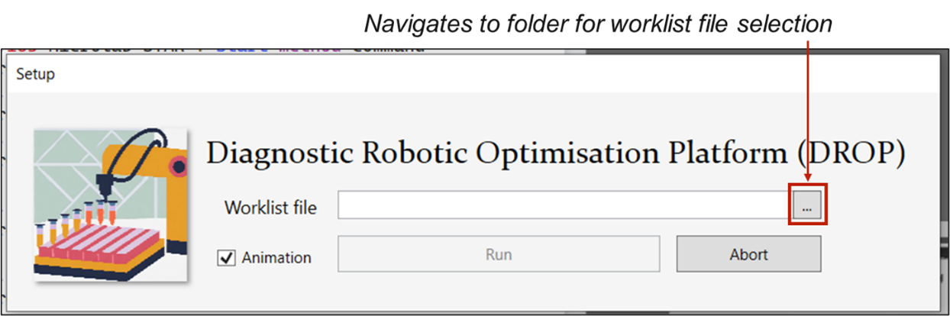
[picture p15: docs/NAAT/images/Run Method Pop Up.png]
Run Pop Up
     <br>
    <small>Figure 6. Pop-up window once the method is started. Load the worklist file from a location on the local machine. Animation can be selected or deselected depending on operator preference. Click the “Run” button to start the operation.</small>

5. When the tip counters appear, update the count for each tip type by clicking on the first available tip in each rack.
Note that insufficient virtual tips will cause the method to error. For simulation runs, best practice is to fill all positions for each tip type. This helps determine the total number of tips required for the actual experiment. Once all tip counts are updated, click “OK” to proceed.

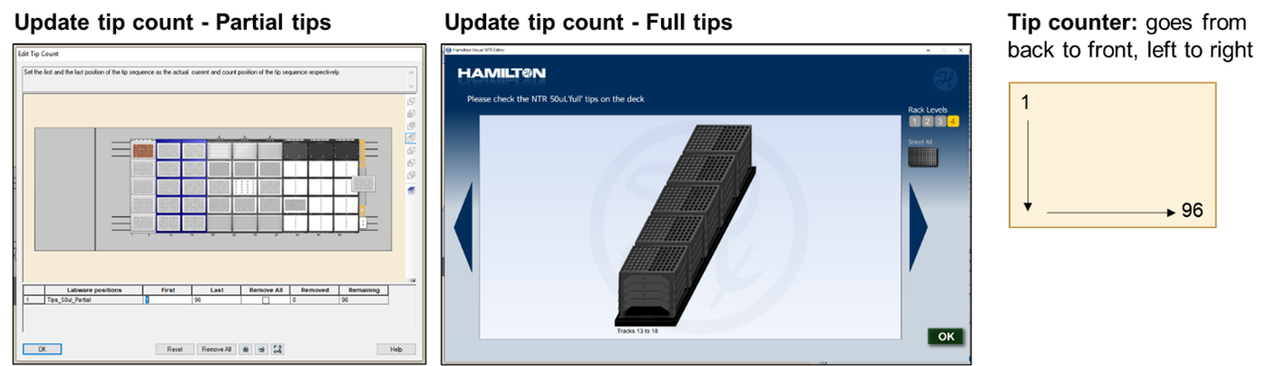
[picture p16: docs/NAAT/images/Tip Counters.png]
Tip Counters
     <br>
    <small>Figure 7. Example pop-up windows that appear to indicate what tips are present on the deck. Make sure enough tips are loaded virtually to cover the steps written in the worklist. This can be checked in Simulation Mode.</small>

6.  Run simulation and observe for any potential errors. 
     
    !!! note 
        - Errors in the worklist can prevent the method from running to completion, and a notification will appear with information to fix the error. 
        - Common errors include having the wrong liquid class for the volume or dispense type selected, choosing a location that doesn’t exist on the deck, or having incorrect group numbering. Other errors will allow the worklist to run without errors but still indicate a problem with the worklist. These errors are typically due to incorrectly noting the plate or well number on the deck. More information about these errors can be found in the Troubleshooting section.
        - There are a few different windows that can be present during simulation.  It is recommended to focus on the “Instrument” window and the “Traces” window. These two windows will allow the operator to see what is happening and identify the cause of any potential error.  

        *Note: The other optional windows that can be included in the simulation view are the “Activities” and “Scheduler” windows, however these are not useful for the current methods.*

        - The length of the simulation will depend on the type and number of steps included in the worklist. 

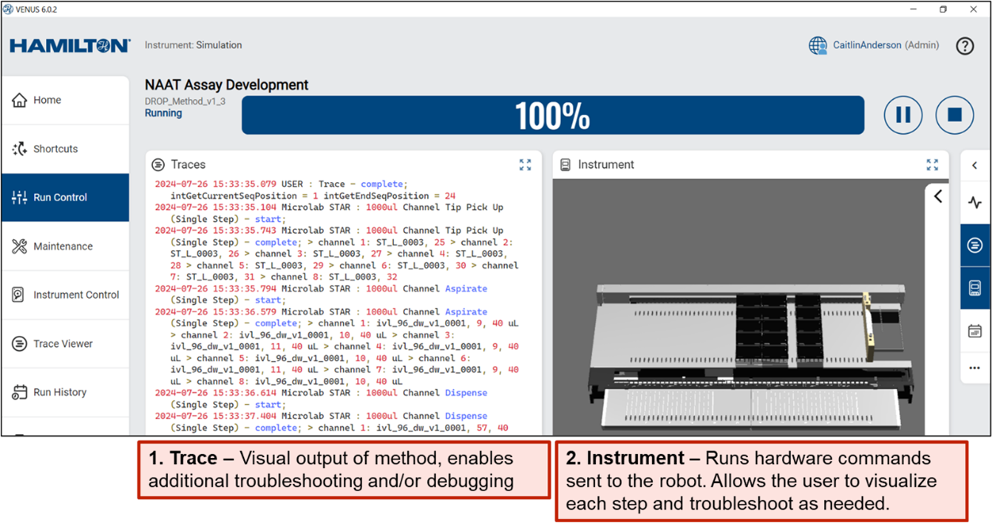
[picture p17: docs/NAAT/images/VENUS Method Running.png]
VENUS Method Running
     <br>
    <small>Figure 8. Run Control when the method is running.</small>

7. Verification and troubleshooting: 
    - If the method runs successfully, a “Method Complete” message will appear. If there are issues, an error message will be displayed.    
    - Note the error and open the logfile to get more information. Once the issue has been identified, refer to the DROP Troubleshooting: Quick Guide document for common problems and how to fix them. 
8. Note the plate and tip locations. 
    - If the run is completed successfully, note the location of the plates and tips used. 
    - It is recommended to take a screenshot and save it into a virtual laboratory notebook to assist with experimental set up. 

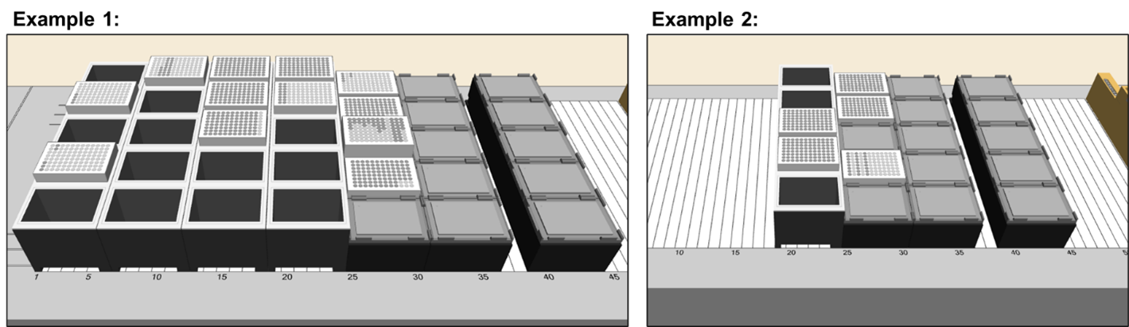
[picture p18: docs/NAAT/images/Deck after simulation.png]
Deck after simulation
 <br>
<small>Figure 9. Example screenshots of methods run on the Hamilton Method. An ideal screenshot will show both the number of tips used and the plate locations that are required.</small>

## :material-robot-industrial: **Run Experiment**

1. Before running an experiment, it is recommended to run daily maintenance. To do so, launch the Instrument Maintenence Program and follow the step by step instructions provided. 
2. If required, turn on the cooling pump at least 1 hour before the experiment to ensure that the carreirs have reached the required temperature. Make sure there is enough liquid in the chiller. 
3. Wipe down the deck with an appropriate cleaning solution. 
4. Add a new biohazard bag intot he waste container. 
5. Ensure there are no potential obstructions to the movement of the channels. 
6. Set up labware according to the deck layout as required by the corresponding Layout and Worklist files. 
7. Load pipette tips into their respective locations. The number of tips required can be determined from the simulation run. 
8. Load all reagents and materials onto the deck. Verify that each piece of labware fits correctly. 
9. Close the front shield of the instrument and verify there is no interference nearby. 
10. Open VENUS software and return to the Home Page in the Navigation Bar. Load the method by selecting the shortcut or by choosing from "Run History". 
11. Confirm that VENUS software is in insturment mode by noting the name listed next to "Instrument" in the Run Control Window. 

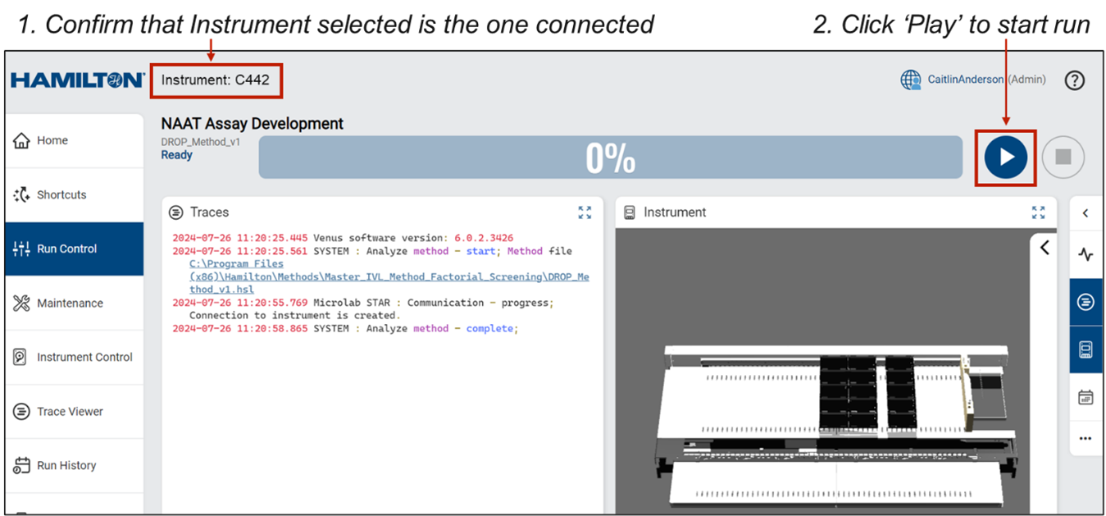
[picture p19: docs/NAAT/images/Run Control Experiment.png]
Run Control Experiment
     <br>
    <small>Figure 10. The view in Run Control when an experiment has been started in instrument mode. Note the machine’s ID to ensure that the system is connected to the Hamilton STAR.</small>

12. Select the blue play button to begin the run. 
13. The pop up shown in figure 6 will appear. Select the worklist file that corresponds to the experiment and select "Run". 

    !!! note 
        The method can be run with or without animation when in instrument mode. 

14. Using insights from the simulation run, , confirm the number of tips required for the experiment. Update the tip count for each tip type by selecting the first available tip in each rack. Be precise—accurate tip counts are essential for successful execution.
Once all tip counts are updated, click “OK” to proceed.
15. Run the method, monitor the instrument and/or the trace for any potential errors. For first-time runs of a new worklist, remain near the instrument to respond quickly in case of any incidents. If a problem occurs, use the “Pause” or “Abort” buttons in the Run Control window to stop or interrupt the process safely.
  
    !!! note 
        Make sure there are enough pipette tips on the deck for the experiment programmed. The system will not notice that there are not enough tips until it runs out.   
  
16. If an error message appears, refer to the Troubleshooting section for assistance. 
17. Clean up:
    - Remove all consumables except for tips from the deck. 
    - Seal all plates (especially any plates containing template) and place immediately in biohazard. 
    - Remove biohazard bag, tie, and place immediately in biohazard bin. 
    - Spray down deck with ethanol and/or bleach (experiment/sample dependent)
    - Clean up any spills and debris, as necessary. 
    - Turn off the cooling pump if used. 

!!! note "General Precautions"
    - Do not insert arms and hands when the robot is running. 
    - Do not switch tubes around once processing has begun. 
    - Do not reuse tips that have been discarded into the waste.
    - Do not empty the tip waste while the instrument is running. 
    - Do not leave tips on the pipetting channels for extended periods (such as overnight).
    - Shield the instrument from direct sunlight or intense artificial light. 
    - Do not place anything on the deck higher than 145mm above the deck’s surface.
    - Close the front cover during the run. The front cover is monitored by software and will abort the method if left open. 
    - Low volume (10µL) tips do not reach the deck or the bottom of sample tubes in standard sample carriers
    - Load tips correctly. 50µL and 300µL tips have the same shoulder height and cannot be used interchangeably.
    - Depending on the assay, certain chemistries are more stable on the deck when stored at 4°C than others. Additional chemistry specific testing may be required. 

## :material-virus: **Testing for Contamination** 

If you suspect contamination in your Hamilton Star liquid handling robot:

1.	Stop the operation: Immediately halt any ongoing processes to prevent further contamination.
2.	Identify the source: Determine where the contamination might have occurred (i.e., from the liquid samples, pipette tips, the environment, etc).
3.	Clean the system:
    - Pipette tips: Replace all pipette tips; discard the contaminated ones and use new, sterile tips.
    - Deck and surfaces: Clean all surfaces of the robot, including the deck and any other areas that might have come into contact with the contaminating material. Use cleaning agent appropriate to the contaminating material (refer to section 9.6 of DROP SOP-001)
4.	Check for residual contamination: After cleaning, run a test with no template control or NTC for NAAT, or blank reactions inside the system to ensure that the contamination has been fully removed.
5.	Prevent future contamination:
    - Regular maintenance: Perform regular maintenance and cleaning as recommended by Hamilton.
    - Proper handling: Ensure that all samples and reagents are handled properly to avoid introducing contaminants.
    - Environmental controls: Maintain a clean working environment to minimize the risk of contamination.

If the contamination persists or unsure about any steps, contact Hamilton’s technical support for further assistance.

<small>
[1] https://www.jmp.com/en/statistics-knowledge-portal/design-of-experiments </small>

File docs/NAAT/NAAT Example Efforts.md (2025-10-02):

The DROP system offers broad utility for research and development efforts focused on NAAT assays. Its specialized module, affectionately named RoboNAAT, has been designed to support large-scale experiments for both PCR and isothermal amplification methods. This document includes an example effort involving a SARS-CoV-2 Loop-Mediated Isothermal Amplification (LAMP) assay, demonstrating the platform’s capabilities in streamlining assay optimization and characterization.

Loop-Mediated Isothermal Amplification (LAMP) is an isothermal amplification technique that uses 4 to 6 primers to target and amplify DNA or RNA at a constant temperature, typically between 60–65°C. The method employs a strand-displacing DNA polymerase, which enables efficient amplification without the need for thermal cycling. Unlike PCR, which generates a predictable and uniform amplicon, LAMP produces a variety of complex amplicon structures. This structural diversity offers advantages—such as increased amplification probability—but also presents challenges, including a higher risk of off-target amplification.

Given the complexity of LAMP chemistry, it is well-suited for optimization using the RoboNAAT system. Traditional one-factor-at-a-time (OFAT) approaches may not fully capture the intricate interactions within a LAMP assay. In this example, the RoboNAAT platform is used to demonstrate: (1) Mastermix optimization, (2) additive screening, and (3) assay evaluation are all demonstrated with their example worklists and results. 

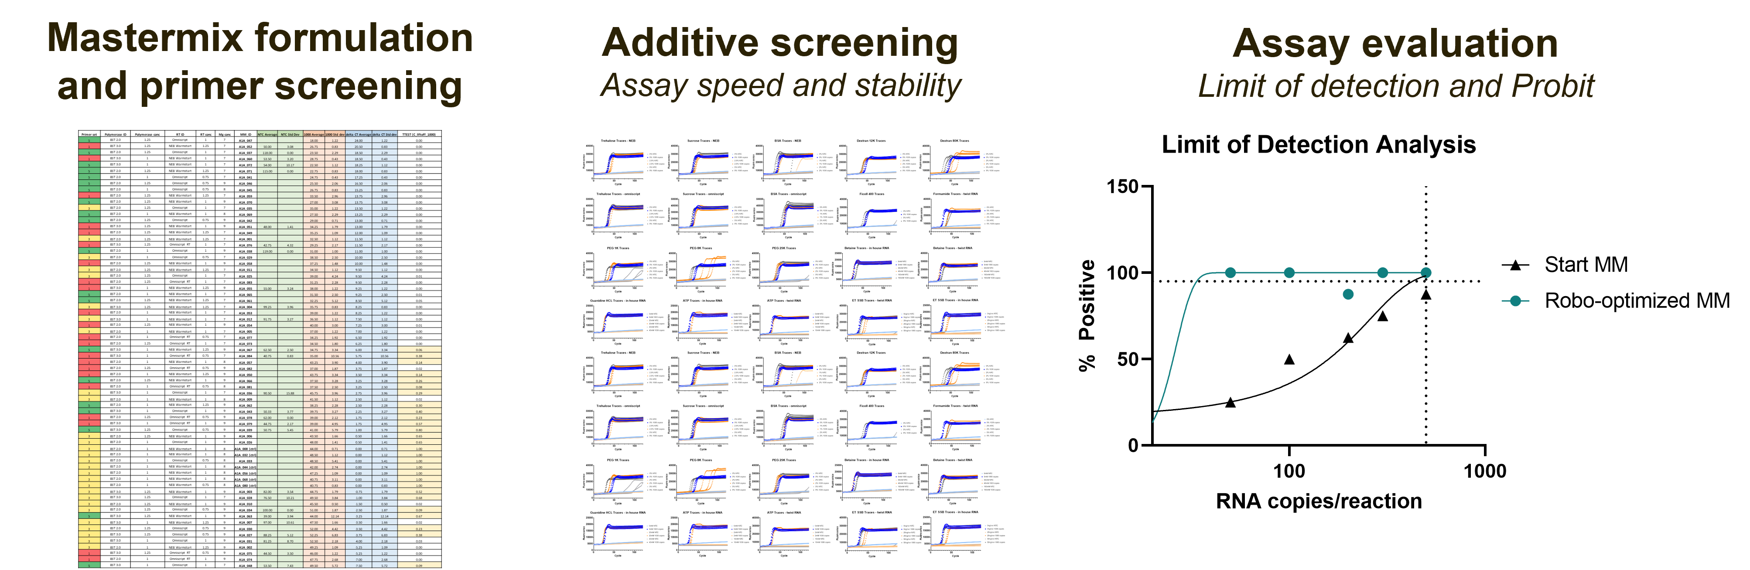
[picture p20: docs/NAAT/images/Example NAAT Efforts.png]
SARS-CoV-2 LAMP Optimization Summary
 <br>
<small>Figure 1. High level overview of the NAAT optimization efforts described in this page. The efforts were broken into (1) mastermix optimization, (2) additive screening and (3) performance evaluation. </small>

## :simple-graphql: **LAMP Mastermix Optimization Effort**

### Experimental Design

The first step in the optimization process for the SARS-CoV-2 LAMP assay was to optimize the best reagents and optimal concentrations for:

- Polymerase (NEB BST 2.0 or 3.0)
- Reverse transcriptase (Omniscript RT or NEB WarmStart RTx)
- Primer sets (L1, L3, and L5)
- Magnesium 

A Definitive Screening Design (DSD) was employed to identify reagent conditions that yielded the fastest time-to-positive without increasing off-target amplification. Using JMP software, the estimated statistical power for all tested variables ranged between 0.99 - 1, indicating high confidence in the results.

The starting mastermix conditions, based on recommendations from New England Biolabs (NEB), were used as a control and included on every plate. In total, 84 mastermix formulations were tested—including the control—across six PCR plates. For each mastermix, four technical replicates were run for both negative controls and positive samples (1,000 copies/µL).

### Reagent Preparation

Three LAMP primer sets were designed using Geneious software and published sequences of the SARS-CoV-2 genome. Primers were ordered from IDT. 

Reagents required for this effort included:

- 10X Isamp buffer
- MgSO4 diluted to 100mM working stock
- dNTP mix (NEB)
- Nuclease free water
- Evagreen (20X)
- NEB BST 2.0 and 3.0
- Omniscript and NEB Warmstart RT
- Primers (IDT)
- PCR plates
- PCR plate seals 

### Worklist Preparation and Validation

Worklists were prepared to run the experiment as designed by JMP. This effort was run using 96 well plates and prepared two at a time. The worklists for preparing the mastermix and aliquoting sample were seperated to enable sample preparation to occur while the mastermix is being run. This effort could be accelerated by using a 384 well plate or if there are more thermocyclers available. 

*Run 1*
:material-microsoft-excel: [Make, mix, and aliquot mastermix](https://github.com/Global-Health-Labs/DROP/blob/main/examples/NAAT/A1A_makeandmix_worklist.csv)
:material-microsoft-excel: [Aliquot Sample](https://github.com/Global-Health-Labs/DROP/blob/main/examples/NAAT/A1A_template_aq_worklist.csv)

*Run 2*
:material-microsoft-excel: [Make, mix, and aliquot mastermix](https://github.com/Global-Health-Labs/DROP/blob/main/examples/NAAT/A1A2_makeandmix_worklist.csv)
:material-microsoft-excel: [Aliquot Sample](https://github.com/Global-Health-Labs/DROP/blob/main/examples/NAAT/A1A2_template_aq_worklist.csv)

*Run 3*
:material-microsoft-excel: [Make, mix, and aliquot mastermix](https://github.com/Global-Health-Labs/DROP/blob/main/examples/NAAT/A1A3_makeandmix_worklist.csv)
:material-microsoft-excel: [Aliquot Sample](https://github.com/Global-Health-Labs/DROP/blob/main/examples/NAAT/A1A3_template_aq_worklist.csv)

*Run 4*
:material-microsoft-excel: [Make, mix, and aliquot mastermix](https://github.com/Global-Health-Labs/DROP/blob/main/examples/NAAT/A1A4_makeandmix_worklist.csv)
:material-microsoft-excel: [Aliquot Sample](https://github.com/Global-Health-Labs/DROP/blob/main/examples/NAAT/A1A4_template_aq_worklist.csv)

For all four of these runs, they have similar deck layouts. Examples of the wells and plates used for both worklist types are in the images below. 

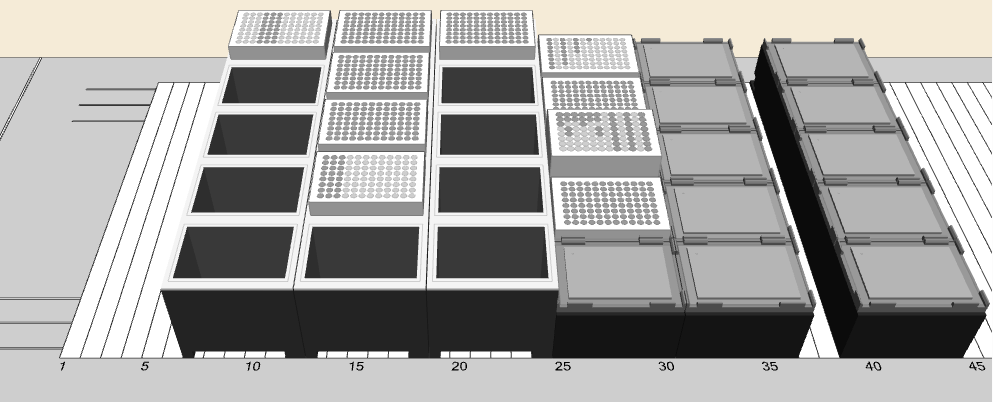
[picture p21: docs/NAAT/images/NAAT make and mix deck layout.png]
Make and mix deck layout
 <br>
<small>Figure 2. Deck layout from the make, mix, and aliquot worklist after running in simulation. </small>

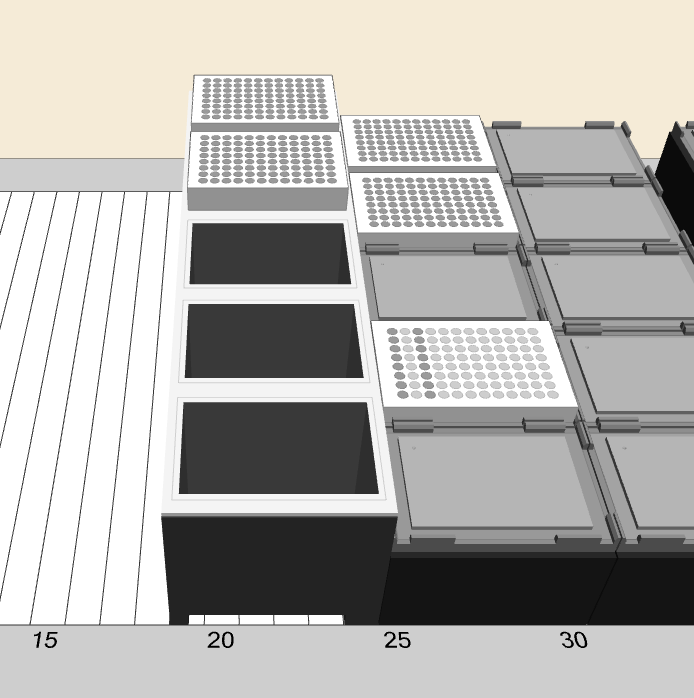
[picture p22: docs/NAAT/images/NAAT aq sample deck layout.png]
LAM 10x10 Screening Results
 <br>
<small>Figure 3. Deck layout from the sample aliquot worklist after running in simulation. </small>

All reagent plates were prepared with the reagents detailed in the worklist viewer in the RADA app. This includes all mastermix components and samples (negative and positive). Tips were loaded onto the deck corresponding to the number identified in the simulation run. The validated worklist(s) were then run on the Hamilton STAR using the VENUS software.

### Results and Conclusions

From this screening effort, 31 master mix formulations demonstrated improved performance compared to the control. 

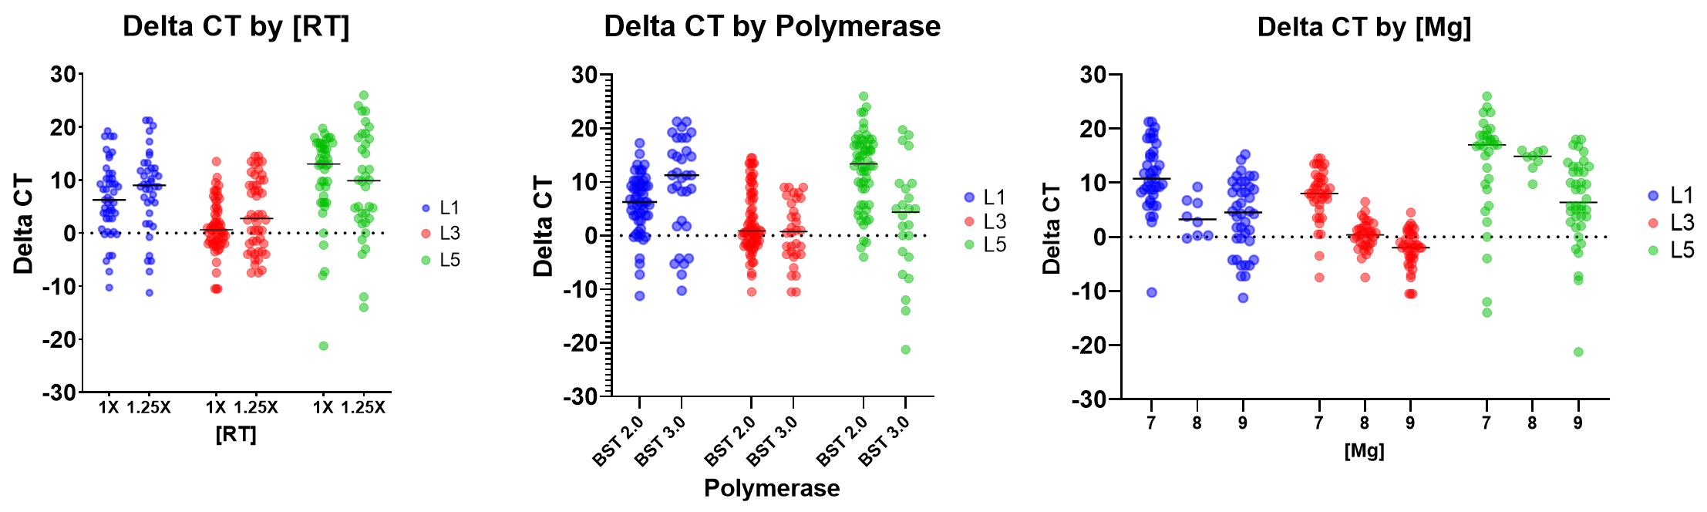
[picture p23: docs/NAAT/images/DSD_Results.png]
DSD Screening Results
 <br>
<small>Figure 4. Snapshot of the data generated from the Definitive Screening Design to identify optimized conditions for the SARS-CoV-2 LAMP assay. </small>

Three key trends emerged:

- Increasing reverse transcriptase concentration had minimal impact on time-to-result across all three primer sets tested.
- Bst 3.0 polymerase enhanced reaction speed for primer set 1, but showed no significant benefit for sets 3 or 5.
- Primer sets 1 and 3 amplified more efficiently at 7 mM Mg²⁺, whereas set 5 did not exhibit a strong response to this condition.

This comprehensive evaluation of over 80 master mix formulations provided deeper insight into LAMP assay behavior. The two top-performing assay conditions were selected for further testing and validation.

## :material-graph: **LAMP Additive Screening Effort**

### Experimental Design

The Additive Screening round aimed to evaluate the impact of various additives on assay speed, inhibitor tolerance, and stability. Most additives tested fell into one of three functional categories:

1. Stability and blocking agents
2. Crowding agents
3. Melting temperature (Tm) and secondary structure reducers

Due to the distinct roles of each category, the experimental design included two approaches:

- Each additive was evaluated individually at two concentrations.
- A Definitive Screening Design (DSD) was used to assess combinations of additives within the stability and blocking category. 

### Reagent Preparation

In addition to the reagent preparation described in the previous effort, a long list of additives and crowding agents were identified for screening. These reagents include:

**Stability agents:**

- Sucrose
- Trehalose 
- BSA

**Crowding agents:**

- PEG (1000, 3000, and 8000)
- Ficoll (400)
- Dextran (12k, 80k, and 410k)

**Tm and secondary structure reducers:**

- Formamide
- Betaine
- DMSO
- SSBs 

**Miscellaneous:**

- ATP
- Guanidine
- EDTA

### Worklist Preparation and Validation

The additive screening was split into three robot runs, preparing two 96 well plates each run. Examples of the worklists are included below for the first two runs. 

*Run 1*
:material-microsoft-excel: [Make, mix, and aliquot mastermix](https://github.com/Global-Health-Labs/DROP/blob/main/examples/NAAT/2a_makeandmix_worklist.csv)
:material-microsoft-excel: [Aliquot Sample](https://github.com/Global-Health-Labs/DROP/blob/main/examples/NAAT/2a_template_aq_worklist.csv)

*Run 2*
:material-microsoft-excel: [Make, mix, and aliquot mastermix](https://github.com/Global-Health-Labs/DROP/blob/main/examples/NAAT/2b_makeandmix_worklist.csv)
:material-microsoft-excel: [Aliquot Sample](https://github.com/Global-Health-Labs/DROP/blob/main/examples/NAAT/2b_half_template_aq_worklist.csv)

### Results and Conclusions

The additive screening approach provided valuable insights into factors that influence time to amplification, off-target amplification, and tolerance to stability agents—particularly those relevant for lyophilization. 

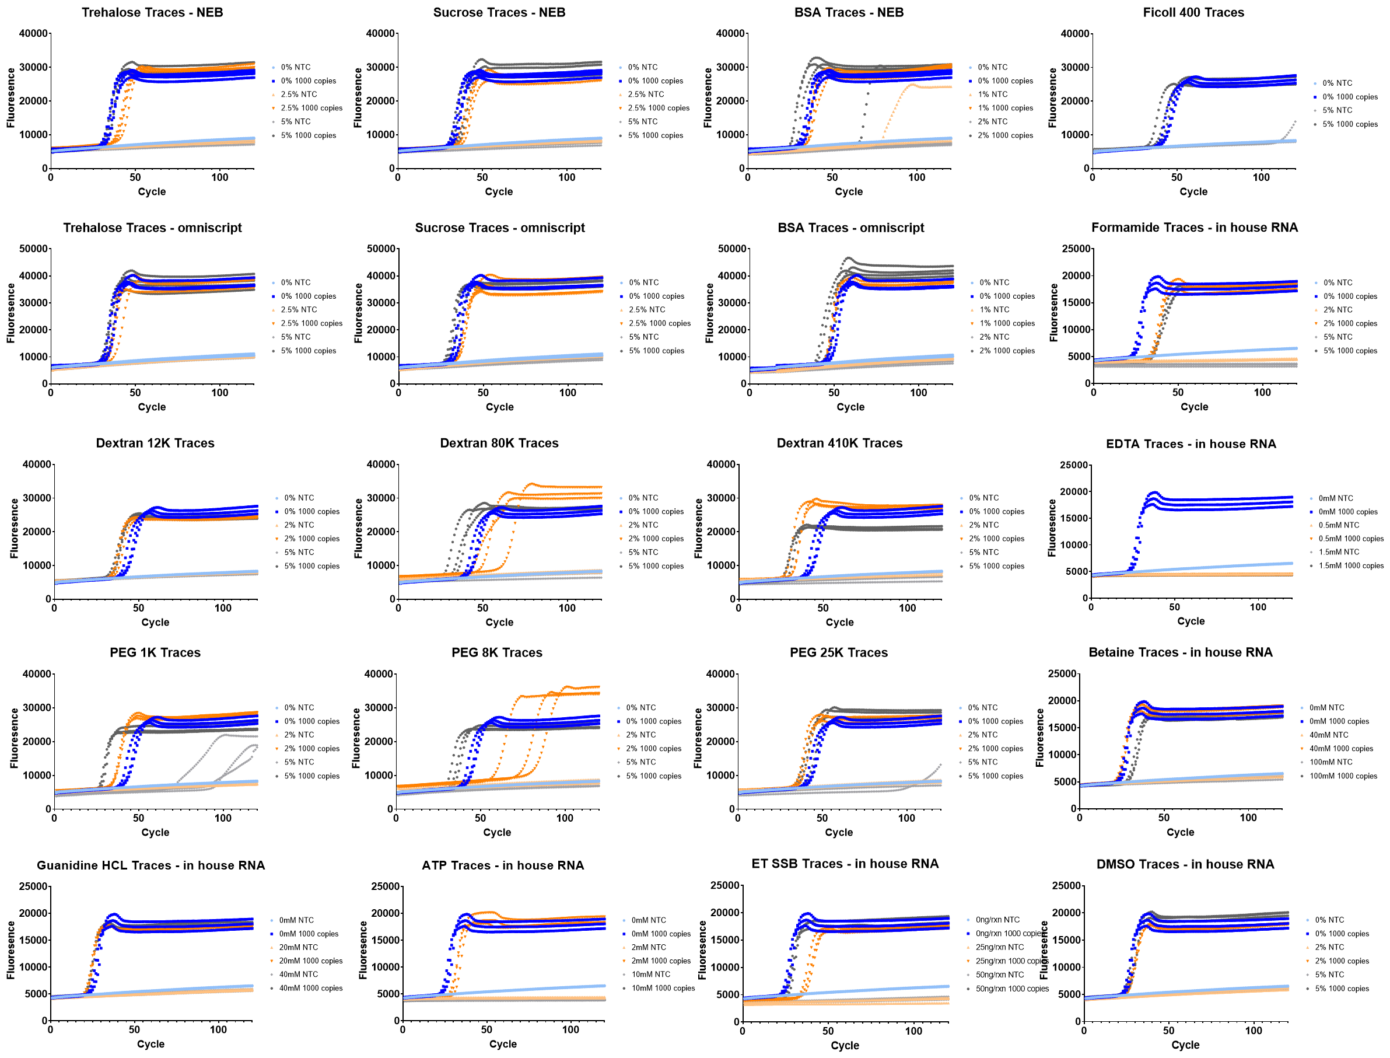
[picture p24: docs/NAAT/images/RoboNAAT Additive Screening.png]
Additive Screening Results
 <br>
<small>Figure 5. Snapshot of the data generated from the Additive Screening to identify optimized conditions for the SARS-CoV-2 LAMP assay. </small>

The quantity of data generated in such a short amount of time highlighted the need for good processes for data analysis and interpretation. Some example observations that were made are included below. 

Stability agents:

- Trehalose and sucrose slowed the reaction slightly at 2.5%, but performance was restored at higher concentrations (5%). 
- BSA at 2% destabilized the reaction and increased variability.

Crowding agents: 

- The crowding agents tested mostly lead to a decrease in time to result (improvements ranging from 5 to 15 cycles for conditions tested), however some conditions had an increase in variability across replicates or an increase in off-target amplification in the negative controls.
- The best improvement was seen from the addition of PEG1K and Dextran 410K, which had average reduction in CT of 15 (with NTCs coming up at ~ 92 cycles) and 15 (w/o NTCs coming up) respectively. 

Secondary structure, Tm reducers, and others: 

- Formamide slowed reaction speed by ~10 cycles.
- Betaine at 40mM had no significant impact on the assay, while 100mM slowed the reaction slightly.
- DMSO had no significant impact on assay at 2 or 5%.
- EDTA at 0.5 and 1.5mM inhibited amplification entirely. This was a surprising result as this reagent has worked great for another LAMP mastermix. 

## :octicons-graph-16: **LAMP Performance Evaluation**

### Experimental Design

The top mastermix condition as determined by the efforts from mastermix concentration optimization and additive screening was evaluated using an LOD against the starting mastermix. The two conditions are:

- Start mastermix: 1X RT, 1X BST 2.0, 8mM Mg
- Optimized mastermix: 1.25X RT, 1.25X BS 2.0, and 7mM Mg 

To generate enough data for the LOD, 8 replicates were run at each concentration tested ranging from 25 - 500 input copies. This range had previously been identified as the dynamic range in which the LOD was likely to be determined.  

LOD example <br>
<small>Figure 6. Informational graphic describing the important concentrations in determining the LOD of an assay. From https://doi.org/10.1016/j.watres.2016.03.026 </small>

### Reagent Preparation

This effort used the same reagents as the mastermix optimization and additive screening efforts. 

### Worklist Preparation and Validation

The performance evaluation was completed with a single robot run. 

:material-microsoft-excel: [Make, mix, and aliquot mastermix](https://github.com/Global-Health-Labs/DROP/blob/main/examples/NAAT/NAAT_LOD_makeandmix_worklist.csv)

:material-microsoft-excel: [Aliquot Sample](https://github.com/Global-Health-Labs/DROP/blob/main/examples/NAAT/NAAT_LOD_template_aq_worklist.csv)

### Results and Conclusions

From this evaluation, it was identified that the optimized mastermix had a 20 fold improvement in LOD as compared to the starting mastermix, with the optimized mastermix and starting mastermix having LODs of 25 and 500 copies/reaction respectively. This is a significant improvement, and was possible after only a couple weeks of hands on work. Additional optimization efforts in a smaller experimental space may provide even more benefits to LOD and/or time to detection. 

LOD example data <br>
<small>Figure 7. Example data from an LOD effort comparing the starting LAMP mastermix to the roboNAAT optimized one. In this effort, the LOD was improved 20-fold from the NEB recommended LAMP conditions. </small>

While this effort only ran 8 replicates for each concentration, the roboNAAT system has also been used to run probit analyses comparing the performance of different mastermixes. A probit analysis typically requires 20 replicates run for each concentration, which can be very challenging to set up manually. 

These efforts, which included mastermix optimization, additive screening, and performance evaluation, are all pieces required when making a NAAT assay. By streamlining and automating these protocols, it is possible to gain more information about a chemistry in less time than using the traditional manual methods. This is particularly powerful as new isothermal amplification methods are developed, to inform research and development efforts and (hopefully) support products making it to market faster.

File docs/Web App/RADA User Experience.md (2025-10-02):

The RADA application features two distinct experiment tabs, one for LFA experiment and another for NAAT experiments. There are separated due to differences in the experimental design, especially regarding the addition of non-plate based hardware. Modifications can be made to widen the range of protocols that RADA can generate as needed.

RADA Main Page <br>
<small>Figure 1. Home page of RADA web application. LFA and NAAT tabs contain experiments for their respective chemistries. </small>

## User Experience - LFA experiment 

Generated LFA experiments can be found in the LFA tab. A new experiment can be generated by selecting "New Experiment" or by copying an existing experiment. 

### :material-test-tube: **Input experimental details**

Fill out the information required on the "New LFA Experiment" page (Figure 2). 

LFA new experiment <br>
<small>Figure 2. Create a new LFA experiment allows the user to input information required for a given experiment. </small>

The items that need to be filled out include:

- Name of experiment 
- Deck layout
- Assay plate configuration 
- Number of technical replicates
- Option to make an experiment preset that will appear in the "New Experiment" drop down. 

Both the Deck Layout and Assay Plate Configuration dropdown menus are populated with predefined setups created by RADA administrators. These configurations help standardize experiment setup and ensure compatibility with automated workflows.

Deck Layout refers to the layout of plates and tubes on the Hamilton deck. The deck layout must be consistent between the web application, the Hamilton Layout file, and the physical location of items on the Hamilton STAR.

Assay Plate Configuration refers to the assay holder (cassette, strip, etc) corresponding to the experiment being run. 

Once the Deck Layout or Assay Plate Configuration have been selected, a preview of the selected configuration will be visible when hovering over the preview icon. 

LFA Deck Layout <br>
<small>Figure 3. Hover over the icon to preview the selected deck layout. </small>

LFA Assay Plate Configuration <br>
<small>Figure 4. Hover over the icon to preview the selected assay plate configuration. </small>

Once completed, select "Save and Continue". 

The next page allows the user to Configure the LFA experiment steps. The form will pop up with one step, and more steps can be added by selecting the "Add step" button on the bottom right. 

The information required for each step include:

- Step name.
- Liquid type to be pipetted. Select "Imaging" if the step is an imaging step. 
- Volume to be pipetted. Note: Numbers can use decimals and are recommended to be between 1-1000uL for the current configuration. 
- Time delay in seconds if a time delay is required between this and the subsequent step. 
- Variable conditions for the experiment. The worklist generator will take the input variables and use a full factorial DoE to run all combinations of the input conditions. Keep an eye on the number of conditions and number of replicates to ensure that there are enough spots on the given deck layout to run the desired experiment. 

Configure LFA Experiment Steps <br>
<small>Figure 5. Screen to load LFA experiment steps. </small>

Configure LFA Experiment Steps Example <br>
<small>Figure 6. Screen with an example of loaded experiment steps. </small>

The order of the steps can be adjusted by using the icon with six dots on the left of the Step Name. 

Once the experiment details are finalized, select "Save and Continue"

### :fontawesome-solid-file-csv: **Download worklist file(s)**

Worklist file can be downloaded from the "Export Experiment" page. This file serves as the input for controlling the Hamilton Venus run.

Download Worklist Files <br>
<small>Figure 7. Export Experiment Files Page. </small>

!!! note
    The downloaded file is a CSV UTF-8. The DROP method does not recognize CSV UTF-8; the downloaded worklist must be saved as a plain .csv file. 

### :material-view-grid-plus-outline: **View robot instructions to load deck**

To enter the Worklist Viewer, select "View Instructions". This viewer contains all the information to correctly load reagents into plates and position the plates on the deck in their designated locations.

Worklist Viewer <br>
<small>Figure 8. Page designed to support the set up of the reagents and plates onto the Hamilton Deck. </small>

Once an experiment is created, it is saved in the application's built-in database. Experiments can be referenced at any time after creation and maybe modified or reloaded as needed. Additionally, completed experiments can be loaded with associated LogFiles and experimental data for further analysis or review.

Worklist Viewer <br>
<small>Figure 9. Experiment summary for example LFA experiment. </small>

## User Experience - NAAT experiment 

All generated NAAT experiments can be viewed in the NAAT tab. To create a new experiment, select "New Experiment", or duplicate an existing one using the copy option. Presets for commonly used protocols are also available in this tab to streamline setup.

### :material-test-tube: **Input experimental details**

Fill out the information required on the "New NAAT Experiment" page (Figure 10). 

NAAT new experiment <br>
<small>Figure 10. Create a new NAAT experiment allows the user to input information required for a given experiment. </small>

The items that need to be filled out include:

- Name of experiment 
- Deck layout
- Number of samples: this number should include the negative control
- Number of technical replicates 
- Mastermix volume: the volume of mastermix only per reaction, not the total reaction volume
- Sample volume
- Liquid type for mastermix liquid
- Liquid type for sample liquid 
- Liquid type for mixing step of mastermix (especially important if the mastermix contents are highly viscous or containing detergent)
- PCR plates size: dropdown with options for 96 and 384 wells
- Option to make an experiment preset that will appear in the "New Experiment" drop down. 

The Deck Layout drop down menu displays configurations created by RADA. For more details on how these configurations are managed, refer to the Admin Capabilities section.

Once the Deck Layout has been selected, a preview of the selected configuration will be visible when hovering over the preview icon. 

Once completed, select "Save and Continue". 

Configure master mix components. On the next page, users can configure the steps of their NAAT experiment. Each master mix is loaded into a dedicated section, which can include as many components as needed.

The form initially displays one master mix by default. To add additional steps, simply click the "Add Master mix" button located at the bottom right of the page.

The information required for each step include:

- Master mix name
- Source name: the identity of the reagent (i.e. water, buffer, dNTPs, DNA pol, etc)
- Concentration unit: drop down menu with options for concentration value will apply to both the final and stock concentration inputs
- Final concentration desired in mastermix
- Stock concentration: starting concentration for reagent
- Liquid type to be pipetted: drop down menu that correlates with the respective liquid class

The order in which reagents are listed determines the sequence in which they will be added by the machine. To adjust the order, use the six-dot handle on the far right of each step to drag and rearrange items as needed. Similarly, master mix sections can be reordered to match your desired workflow or protocol sequence.

Configure NAAT Experiment Steps <br>
<small>Figure 11. Screen to load NAAT experiment steps, with example information loaded. </small>

To reduce repetitive setup, mastermixes can be copied. This can be done by selecting the three-bar menu located in the upper right corner of the mastermix header. This feature allows for quick duplication and easy modification of existing steps.

Configure NAAT Experiment Steps <br>
<small>Figure 12. Dropdown to allow for addition of reagents to a mastermix, copy or delete the mastermix. </small>

Once the experiment details are finalized, select "Save and Continue"

### :fontawesome-solid-file-csv: **Download worklist file(s)**

Worklist files can be downloaded from the Export Experiment page. These files are used as input for the Hamilton VENUS Run Control system.

The NAAT worklist generator produces two separate files:
Master mix Worklist – handles the mixing and aliquoting of the master mix.
Sample Worklist – manages the aliquoting of the samples.

This separation ensures precise execution and easier troubleshooting during automated runs.

Download Worklist Files <br>
<small>Figure 13. Export Experiment Files Page. </small>

!!! note
    The downloaded file is a CSV UTP-8 type. The DROP method does not recognize CSV UTF-8; the downloaded worklist must be saved as a plain .csv file.

### :material-view-grid-plus-outline: **View robot instructions to load deck**

To enter the Worklist Viewer, select "View Instructions". This viewer contains all the information to correctly load reagents into plates and position the plates on the deck in their designated locations.

Worklist Viewer <br>
<small>Figure 14. Page designed to support the set up of the reagents and plates onto the Hamilton Deck. </small>

The worklist viewer has five sections:

1.	Reagent loading section – This section lists all reagents required for the experiment, including solution name (based on user input), plate name, well number, and a check box to indicate when a reagent has been loaded. Selecting a row will highlight the corresponding locations in both the Plate Layout and Deck Layout. 
2.	Plate Layout – Displays the layout of a given plate, 96 or 384. When selected the corresponding well will be highlighted in black. 
3.	Deck Layout – Shows the robot's deck configuration. When a reagent is selected, the associated plate is highlighted in black, mirroring the Plate Layout behavior. 
4.	Instructions – When a reagent row is selected, this panel provides detailed loading instructions, including: Solution name, volume to be pipetted, well and plate ID. This helps users accurately load reagents with the correct volume and location.

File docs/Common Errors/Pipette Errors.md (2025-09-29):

### Insufficient tips 

+ **Problem**: Did not load enough tips onto deck (virtually) in either simulation or in instrument mode.
+ **Error pop-up**:  An error occured while running Vector. The error description is C:\Program Files(x86)\Hamilton\Library\HSLMlStarStepReturnLib.hsl(401): _Method::StepReturn::GetErrorCode() The parameter is incorrect (0x0 - 0x0 - 0x1)
+ **Logfile information**: The LogFile error will include the following near the end of the LogFile 

>Microlab STAR : Main - error; An error occurred while running Vector.  The error description is: No more positions available in sequence seqTipFull. (0x28 - 0x2 - 0x80d) <br><br>
>Microlab STAR : 1000ul Channel Tip Pick Up (Single Step) - complete with error; An error occurred while running Vector.  The error description is: No more positions available in sequence seqTipFull. (0x28 - 0x2 - 0x80d) <br><br>
>USER : Trace - complete; Tip Pickup Return:  0 <br><br>
>SYSTEM : Execute method - error; An error occurred while running Vector.  The error description is: C:\Program Files (x86)\Hamilton\Library\HSLMlStarStepReturnLib.hsl(401) : _Method::StepReturn::GetErrorCode() The parameter is incorrect. (0x0 - 0x0 - 0x1)

+ **Solution**: Load more tips onto the deck. If there are not enough positions on that specific layout for the number of tips required to run the worklist, make an updated layout file with the correct number of pipette tip positions (in increments of 96). The sequence referenced can also include seqTipPartial if the sequence that does not have enough positions is a partial tip sequence. 

### No liquid detected

+ **Problem**: No liquid is detected when the pipette goes into the well to either aspirate or dispense. 
+ **Error pop-up**:  1000ul Channel Aspirate - Error > Description: Liquid level not found. 
+ **Logfile information**: The LogFile error will include the following near the end of the LogFile 
+ **Solution**: 

    - This problem can be fixed in a couple ways. If this is an error that should not appear at this step for any reason, look to see if previous pipetting steps delivered the correct volumes. An example would be if you had the wrong liquid class selected for a viscous liquid, causing the robot to pipette too little volume. This would lead a mastermix to have insufficient volume, which can be easily confirmed by looking at the volume of your viscous liquid remaining in the stock plate.   
    - Typically, though, we see this error because the robot is looking for a liquid level higher than where it is. Therefore, fix this by selecting the "Bottom" button. Then click "Execute". This will send the pipette tip to the bottom of the well (and then raise up slightly to enable pipetting) instead of looking for the liquid level and bypass this issue. 

### Pipette does not reach labware bottom

+ **Problem**: Pipette tip doesn’t reach the bottom of the labware, therefore requiring large amounts of dead volume in the well plates than what should be required. 
+ **Error pop-up**:  First sign of an error is typically that the volume pipetted is lower than programmed. Can be identified by visually watching how far into the well plate or onto the LFA that the pipette tip goes. 
+ **Logfile information**: NA
+ **Solution**: Teach the position of the labware to the appropriate height. Contact GH Labs or IGB application specialist for support in teaching labware positions. 

### Incorrect pipette tip assignment

+ **Problem**: The system is expecting a certain pipette tip, and a different one is in the identified location. 
+ **Error pop-up**:  If the issue is between 50 and 300 uL tips, then non error will pop up but the system will run assuming that it is using a tip with different dimensions (height) and may either crash or be unable to reach the liquid level. 
+ **Logfile information**: None if the issue happens with 50 and 300 uL tip. Will identify that it can not pick up the tip if it is between 50/300 and 1000 as their shoulder heights are different. 
+ **Solution**: Ensure that the tips loaded on the deck are the ones identified in the Hamilton Layout. Pictures of the deck layout or labels on the tip carriers can also reduce the likelihood of error. 

### Tip swap

+ **Problem**: Tips are not in the correct position on the deck. 
+ **Error pop-up**:  For mixups between the 50 and 300uL tips the system cannot differentiate between them. The error that will happen is that the channel will act as though the tip is either much longer or much shorter than it is actually. 
+ **Logfile information**: NA
+ **Solution**: Ensure that pipette tips are loaded in their exact locations as described in the layout file. 

### Channel cannot reach location 

+ **Problem**: Because the camera is installed in the DROP system, channels 1 and 2 cannot reach all locations on the deck. Specifically they are unable to reach the locations closest to the front of the machine.
+ **Error pop-up**:  
+ **Logfile information**: 
+ **Solution**: The deck design can be optimized to reduce the risk of this happening. This is also why most experiments that require the running of LFAs should be in groups of 8.

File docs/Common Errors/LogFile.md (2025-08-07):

So, you have had an error. Now what?
<br> <br>
**The LogFile automatically generated by the Hamilton software will become your best friend.**
<br> <br>
The LogFile is a file that is created every single time a worklist is run, whether it is run in simulation or on the instrument. All LogFiles can be found on the robot computer here - C:\Program Files (x86)\HAMILTON\LogFiles. The file name will include the method that was run, and an alphanumeric value that is 32 characters long. An example is - RoboNAAT_Method_v3_10a7f1fb99e04a18936f6eb2fbc7e4c4_Trace. These files open in the Notepad app, which is already installed on both robot computers. 

There are a couple ways to tell if you have the correct log file, one is by looking for the most recent one (you can tell by what the date modified value is) assuming it was the most recent experiment run. Another is by opening the file and looking for the line that says "fileWorklist =". On the right side of the equation, the location and name of the worklist file loaded will be shown. This is another way to confirm you have the correct file. 

## Common Errors
| Section           | Error | Link     |
| :-------------- | :-------------------------- | :---------------------: |
| `Worklist Error`             | Worklist file not found|[🗊](./Worklist%20Errors.md) |
| `Worklist Error`             | CSV in incorrect format |[🗊](./Worklist%20Errors.md) |
| `Worklist Error`             | Liquid class type mismatch |[🗊](./Worklist%20Errors.md)|
| `Worklist Error`             | Volume outside of liquid class correction curve|[🗊](./Worklist%20Errors.md)|
| `Worklist Error`             | Incorrect group numbering |[🗊](./Worklist%20Errors.md)|
| `Worklist Error`             | Labware definitions incorrect for deck layout|[🗊](./Worklist%20Errors.md)|
| `Pipette Error`             | Insufficient tips loaded (simulation or on instrument)|[💧](./Pipette%20Errors.md)|
| `Pipette Error`             | No liquid detected |[💧](./Pipette%20Errors.md)|
| `Pipette Error`             | Pipette does not reach bottom of labware |[💧](./Pipette%20Errors.md)|
| `Pipette Error`             | Incorrect pipette tip assignment|[💧](./Pipette%20Errors.md)|
| `Pipette Error`             | 50uL/300uL tips swapped |[💧](./Pipette%20Errors.md)|
| `Pipette Error`             | Pipetting channel cannot reach location on deck|[💧](./Pipette%20Errors.md)|
| `Camera Error`             | Camera unable to take or save images due to incorrect library|[📷](./Camera%20Errors.md)|
| `Camera Error`             | Camera unable to take or save images due to lack of space on computer |[📷](./Camera%20Errors.md)|
| `Miscellaneous Error`             | Configuration file gets corrupted|[📍](./Miscellaneous%20Errors.md)|

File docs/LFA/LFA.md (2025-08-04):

## RoboLFA Overview

Lateral Flow Assays (LFAs) are a popular diagnostic technology that enables more sophisticated protein based chemistries to be run at or near the point of care. With low cost and ease of use, the LFA technology has been used for applications that span across a wide range of targets, including bacteria, viruses, toxins, and more. Even though the use of these tests is fairly straightforward, there can be a significant investment required to create high performance LFAs. 

LFA Background <br>
<small>Figure 1. Schematic of a classic LFA, from https://doi.org/10.1007/s00216-022-03897-9. The image depicts the materials involved in an LFA, which often includes a sample pad, a conjugate pad, a test membrane onto which a test and control ine are striped, and a wicking pad to drive flow (A). Typical use involves the addition of a sample and/or buffer to the sample pad, which flows downstream to rehydrate the conjugate dried into the conjugate pad (B). Liquid then moves into the test membrane onto which a test and/or control line will appear depending on whether analyte is present in the sample. All remaining liquid and unbound proteins then flow into the wicking pad. </small>

To address the time and monetary cost involved in LFA research and development, GH Labs developed a development platform utilizing an automated liquid handling system. This system, termed RoboLFA, is a subcategory of the DROP platform. RoboLFA consists of LFA specific hardware, software, and protocols to enable large optimization or characterization expriments with limited hands-on time required. The system is described in more detail in a paper by Anderson et al<sup>[1](https://link.springer.com/article/10.1007/s00216-022-03897-9)</sup>. 

## Custom Hardware 

LFAs can come in a few different forms. We have developed holders to address two of these forms, a strip and a cassette. Other form factors can be integrated, but may require additional development to get a holder that is compatible with both the form factor of the LFA and the form factor of the deck postiions on the Hamilton STAR. These holders may also be adapted to other liquid handling systems. 

LFA Strip Holders <br>
<small>Figure 2. Image of the developed LFA strip (A), (B), and (C), and cassettes (D) from https://doi.org/10.1007/s00216-022-03897-9</small>

### RoboLFA Strip Holder 
An LFA strip holder is helpful when a cassette has not yet been designed or the LFA dimensions are still requiring adjustment. Some LFAs on the market are in strip form, such as *Milenia Biotec HybriDetect Universal Lateral Flow Assays* and over-the-counter HCG tests, and therefore would stay in this category throught the entire research and development lifecycle. On this site we will mostly discuss our most commonly used strip holder, which consists of the following:

- Aluminium plate (dimensions) with six holes compatible with (size) screws  
- 3D printed base plate designed to fit the dimensions of the LFA  
- 3D printed top plate designed with necessary pinch points, wells for reagent addition, and read window   
- 6 Screws (size)

When starting a new RoboLFA effort, it is critical to understand the requirements for a strip holder. This includes the length and width of the strip, the location and thickness of pinch points, the location and volume required for reagent addition, and the location and size of the read window. Each of these factors can be modified in the CAD files linked below. More detailed instructions can be found [here](NEED TO ADD A LINK HERE). 

LFA Strip Holders <br>
<small>Figure 2. Strip holder to hold non-cassetted LFAs. The designed holder consists of three parts, (1) an aluminum base plate, (2) 3D brinted base plate and (3) 3D printed top plate. The bottom plate is designed with guide posts for consistent placement of a strip, while the top plate is designed to have pinch points and wells where required. Image from https://doi.org/10.1007/s00216-022-03897-9</small>

CAD files can be found here: 

We have two other versions of the strip holder that have some usability issues that need to be addressed. The other two strip holders are either challenging to set up reproducibly or require additional engineering on the clamping mechanism. More details about both of these holders can be found in the [supplemental material](https://doi.org/10.1007/s00216-022-03897-9). 
If we were to get additional time to further improve the strip holders, the most exciting holder is the lego inspired assembly that allows for different 3D printed cross bars to be added interchangeably in 0.5mm increments along the length of the holder. 

### RoboLFA Cassette Holder
An LFA cassette holder is used when the strip dimensions have been locked and is further along the R&D pipeline. The cassette holder has defined spacing, allowing for precise liquid delivery and imaging across a large number of LFA devices.  

The cassette holder consists of:  

+ A 1/4" aluminum plate (40 x 48 cm) with the following modifications  
    - Two pins to guide the acrylic sheet in place  
    - Two drilled holes (dimensions) that enable consistent placement of the cassette holder onto the Hamilton Deck  
+ A 1/16" acrylic sheet (40 x 48 cm) with the following modifications
    - Laser cut to fit the cassette dimensions (example CAD files fit 80 and 96 cassettes respectively)
    - Two pin holes to guide ont othe aluminum plate 

LFA Cassette Holders <br>
<small>Figure 3. Holder for cassetted LFAs. The designed holder consists of two parts, (1) an aluminum base plate, (2) a laser cut acrylic sheet designed to fit cassettes with little "wiggle room".  Image from https://doi.org/10.1007/s00216-022-03897-9</small>

CAD link:

The cassette holder requires two additional custom parts: 

+ Hamilton Carrier (product #) with posts (modification) in one slot  - ADD GITHUB LINK
+ Alignment spacers to assist with consistent placement of cassette holder 
    - Spacer 1 - ADD GITHUB LINK
    - Spacer 2 - ADD GITHUB LINK

CAD link: 

## Deck build 

Images of deck build with both the LFA strip holder and the cassette holder 

## Custom Software

### Hamilton Method and Layout

Link to github page

### RADA
link to RADA page? 

### LFA image analysis 

Link to github page

## Running an LFA experiment 
### Adjusting hardware/labware for strip/cassette

### Adjusting RADA for strip

### Adjusting imaging for strip 

### Optimizing liquid classes 
The DROP system has a library of liquid classes that can be used to run experiments. These liquid classes are modified to have the precise pipetting protocol to enable consistent pipetting for a given liquid class. It is important to precisely tune a liquid class for the liquids that will be pipetted during an experiment on the DROP system. Some of the parameters that are included are flow rate, air transport volume, blowout volume, settling time, and more. More information can be found in the CO-RE Liquid Editor Help section. Liquid classes can be made using the Hamilton Liquid Verification Kit (LVK). When more liquid classes are made, or when an existing liquid class is validated for a new liquid, they will undergo performance qualification. The list below includes liquid classes used commonly for the LFA system. 

| Liquid Class           | Tip size | Dispense Type     | Recommended validation for: |
| :-------------- | :-------------------- | :------------------- | :------------------- |
| RoboLFA_tip50_spot_JetEmpty | 50|JetEmpty | Antibody and conjugate solutions |

### Experiment Checklist
***A. Preparing for the experiment:***  
- Design experimental protocol  
- Design, source, and build LFA components  
- Identify and define additional liquid classes or hardware requirements within the Hamilton software, if needed   
- Source appropriate reagents, pipette tips, plates, LFAs, and custom LFA-specific hardware  
- Generate experiment worklist file   
- Validate worklist file in simulation mode within the Hamilton software  
- Make modifications to worklist as needed   
- Note plate locations and number of tips used  
***B. Running the experiment:***  
- Prepare Hamilton STAR instrument deck   
- Spray down deck with cleaning solution  
- Complete Daily Maintenance. Skip, if already completed for the day.   
- Load all required tips onto instrument  
- Load reagents and samples into corresponding plates    
- Place all reagent plates, sample plates, LFAs and associated custom LFA-specific hardware onto Hamilton STAR instrument deck  
- Run worklist(s) on Hamilton STAR using Hamilton software  
***C. Finalizing experiment:***  
- Verify data has been acquired and saved in appropriate folders  
- Clean up Hamilton STAR instrument deck, reusable custom LFA-specific hardware, and dispose of materials appropriately  
- Analyze data using GH Labs image analysis software  
- Prepare documentation of results and analysis   

## References

[1] Anderson, C.E., Huynh, T., Gasperino, D.J. et al. Automated liquid handling robot for rapid lateral flow assay development. Anal Bioanal Chem 414, 2607–2618 (2022). https://doi.org/10.1007/s00216-022-03897-9 <br>
[2] Cate, D. M., Bishop, J. D., Hsieh, H. V., et al. Antibody Screening Results for Anti-Nucleocapsid Antibodies Toward the Development of a Lateral Flow Assay to Detect SARS-CoV-2 Nucleocapsid Protein. ACS Omega 2021 6 (39), 25116-25123. DOI: 10.1021/acsomega.1c01253 <br> 
[3] Cantera, J. L., Cate, D. M., Golden, A., et al. Screening Antibodies Raised against the Spike Glycoprotein of SARS-CoV-2 to Support the Development of Rapid Antigen Assays. ACS Omega 2021 6 (31), 20139-20148. DOI: 10.1021/acsomega.1c01321 <br>

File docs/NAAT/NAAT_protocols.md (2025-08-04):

## Running a NAAT experiment 
### Adjusting hardware/labware

### Optimizing liquid classes 
The DROP system has a library of liquid classes that can be used to run experiments. These liquid classes are modified to have the precise pipetting protocol to enable consistent pipetting for a given liquid class. It is important to precisely tune a liquid class for the liquids that will be pipetted during an experiment on the DROP system. Some of the parameters that are included are flow rate, air transport volume, blowout volume, settling time, and more. More information can be found in the CO-RE Liquid Editor Help section. Liquid classes can be made using the Hamilton Liquid Verification Kit (LVK). When more liquid classes are made, or when an existing liquid class is validated for a new liquid, they will undergo performance qualification. The list below includes liquid classes used commonly for the NAAT system. 

| Liquid Class           | Tip size | Dispense Type     | Recommended validation for: |
| :-------------- | :-------------------- | :------------------- | :------------------- |
| RoboNAAT_tip50_buffer_SurfaceEmpty | 50|Surface Empty | Water, 10X IsoAmp buffers, 100mM magnesium |
| RoboNAAT_tip300_buffer_JetEmpty | 300|Jet Empty | Water, 10X IsoAmp buffers, 100mM magnesium |
| RoboNAAT_tip300_buffer_SurfaceEmpty | 300|Surface Empty | Water, 10X IsoAmp buffers, 100mM magnesium |
| RoboNAAT_tip50_primers_SurfaceEmpty | 50|Surface Empty | Primers, dNTPs, gDNA |
| RoboNAAT_tip300_primers_SurfaceEmpty | 300|Surface Empty | Primers, dNTPs, gDNA |
| RoboNAAT_tip50_enzymes_SurfaceEmpty | 50|Surface Empty | Any enzyme in 50% glycerol, other related viscous liquids |
| RoboNAAT_tip300_enzymes_SurfaceEmpty | 300|Surface Empty | Any enzyme in 50% glycerol, other related viscous liquids |
| RoboNAAT_tip1000_water_JetEmpty | 1000|Jet Empty | Water |
| RoboNAAT_tip1000_water_SurfaceEmpty | 1000|Surface Empty | Water |
| RoboNAAT_tip50_template_SurfaceEmpty | 50|Surface Empty | RNA or DNA template |
| RoboNAAT_tip50_organics_SurfaceEmpty | 50|Surface Empty | Ethanol |
| RoboNAAT_tip50_detergent_SurfaceEmpty | 50|Surface Empty | 5% Triton X-100, Tween-20, and PVP |
| RoboNAAT_tip50_buffer_JetEmpty | 50|Jet Empty | Aliquoting full mastermix |

Best practices include addition of date and liquid class version to the validated liquid class. 

### Experiment Checklist

***Preparing for the experiment:***  
- Design experimental protocol  
- Define additional liquid classes or hardware definitions (if required)   
- Source appropriate reagents, pipette tips, devices and plates  
- Generate worklist    
- Validate worklist in simulation   
- Make modifications to worklist as needed   
- Note plate locations and number of tips used  
***Running the experiment:***  
- Prepare instrument deck   
- Start refrigerated circulator (if required)  
- UV treat and/or spray down deck with cleaning solution  
- Complete Daily Maintenance. Skip, if already completed for the day.  
- Load all required tips onto instrument  
- Load reagents into reagent plates in PCR hood   
- Load all reagent and assay plates required to run experiment onto Hamilton STAR  
- Run worklist(s) on Hamilton STAR   
- Seal assay plate(s)  
- Vortex briefly and spin down assay plate(s)  
- Place assay plate(s) onto thermocycler, load corresponding protocol and run  
***Finalizing experiment:***  
- Clean deck and dispose of materials appropriately  
- Analyze data   
- Repeat as needed   

## References

[1]  <br>
[2]  <br>

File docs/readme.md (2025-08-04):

# Near-Point-of-Care Bead Beater (nPOC-BB)

## Overview

The Near-Point-of-Care Bead Beater (nPOC-BB) is a portable laboratory instrument designed to prepare challenging samples for nucleic acid amplification tests by efficiently releasing amplifiable genomic DNA from difficult-to-lyse microorganisms.

This repository contains the design and data files related to development and evaluation of the nPOC-BB in the context of *Mycobacterium tuberculosis* (Mtb) detection in tongue swab or sputum specimens.

## Documentation

Please [read the docs](https://global-health-labs.github.io/nPOC-BB) to find out more about the nPOC-BB project and its history of development at Global Health Labs. Another overview of this project and other projects developed at Global Health Labs will be collected at [Gates Open Research](https://gatesopenresearch.org/gateways).

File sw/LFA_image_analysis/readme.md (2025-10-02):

# LFA Image Analysis Tool

An automated image analysis system for Lateral Flow Assays (LFAs) designed for the DROP (Diagnostic Robotic Optimization Platform). This tool processes images captured by Hamilton robot systems to quantify test and control lines/spots, providing objective measurements for assay optimization.

## Overview

This software provides automated analysis of LFA images with support for:
- **Multiple signal types**: Lines and spots on lateral flow strips
- **Flexible backgrounds**: Dark frames (custom holders) or light frames (white cassettes)
- **Multi-signal analysis**: Simultaneous analysis of test and control lines
- **Automated and manual ROI selection**: Full automation or manual region of interest selection
- **Batch processing**: High-throughput analysis of multiple experiments
- **Hamilton robot integration**: Direct processing of robot-captured images

## Key Features

- **Versatile Image Processing**: Handles both line-based and spot-based LFA formats
- **Background Adaptability**: Optimized for both dark and light background imaging
- **Multi-channel Analysis**: Supports red, green, blue, and grayscale color channels
- **Automated ROI Detection**: Intelligent region of interest identification
- **Manual Override Capability**: Manual ROI selection for problematic images
- **Batch File Generation**: Automated creation of processing scripts
- **Comprehensive Output**: CSV data files and visualization PDFs
- **Parameter Optimization**: Extensive customization for different strip types

## File Structure

```
LFA_image_analysis/
├── backend.py                       # Core image processing functions
├── Hamilton_image_analysis.py       # Main analysis script for Hamilton integration
├── generate_batch_files_and_run.py  # Batch processing automation
├── Batch_files_and_run.ipynb       # Jupyter notebook for batch analysis
├── requirements.txt                 # Python dependencies
├── all_results.csv                  # Consolidated results from multiple experiments
├── exp3_full_worklist/              # Example experiment 3 data
├── exp4_full_worklist/              # Example experiment 4 data
├── *.bat                           # Generated batch files for automated processing
└── __pycache__/                    # Python cache files
```

## Core Functionality

### Image Processing Pipeline

1. **Image Loading**: Supports standard image formats (PNG, JPG, TIFF)
2. **Initial ROI Detection**: Automated identification of strip regions
3. **Background Correction**: Adaptive processing for dark/light backgrounds
4. **Signal Extraction**: Line or spot detection and quantification
5. **Multi-signal Analysis**: Simultaneous test and control line processing
6. **Data Export**: CSV results and visualization generation

### Signal Types
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

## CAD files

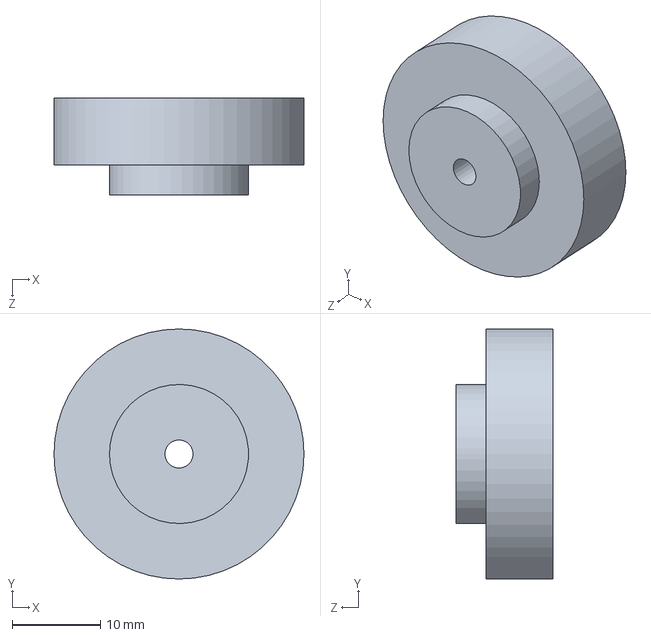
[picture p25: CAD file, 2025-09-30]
hw/CAD models/Custom plates and ancillary pieces/Hamilton_spacer.SLDPRT
28.4 x 28.4 x 11.0 mm

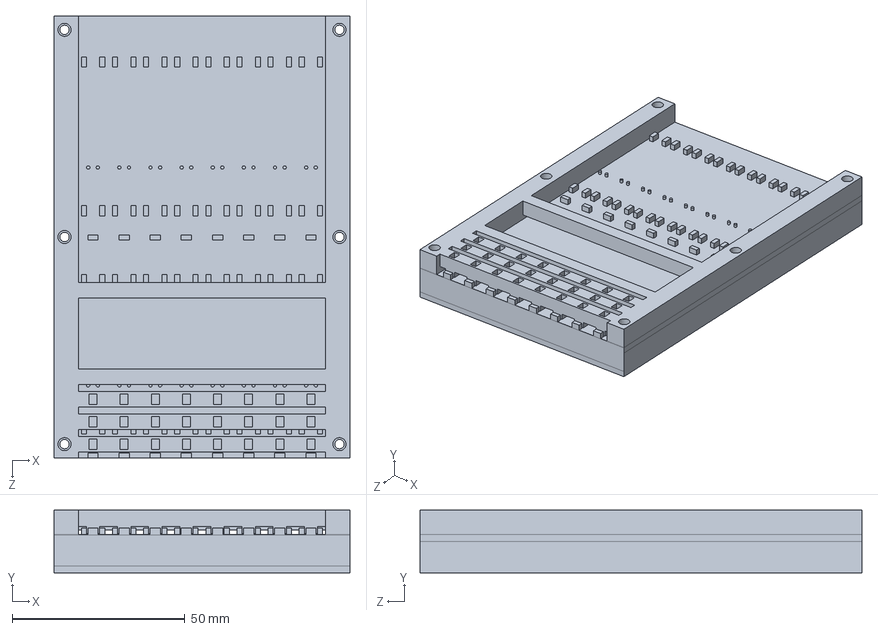
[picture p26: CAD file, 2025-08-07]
hw/CAD models/LFA holders/LFA Holder 3 - top and bottom/v2_strip_holder/strip_tray_v16_wellcombine.SLDPRT
85.5 x 18.1 x 127.8 mm

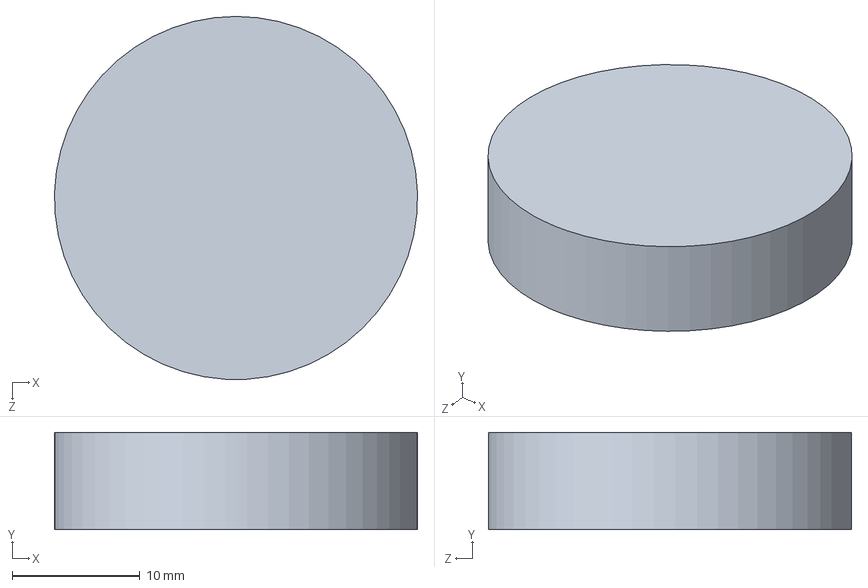
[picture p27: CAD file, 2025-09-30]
hw/CAD models/Custom plates and ancillary pieces/Hamilton_spacer_2.SLDPRT
28.4 x 7.62 x 28.4 mm

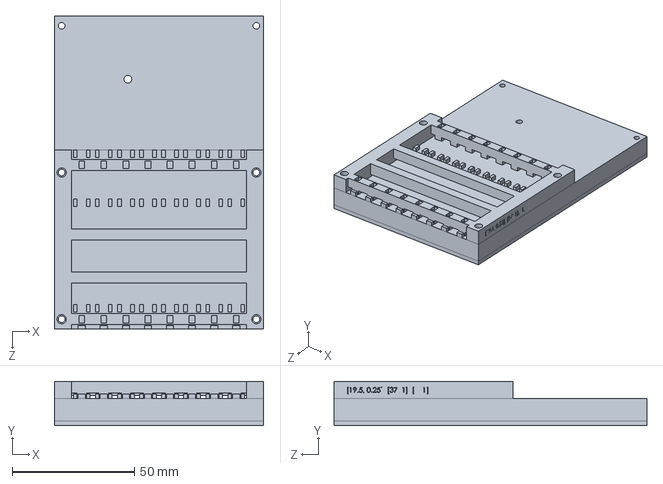
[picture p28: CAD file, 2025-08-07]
hw/CAD models/LFA holders/LFA Holder 3 - top and bottom/v2_strip_holder/strip_tray_v16.SLDPRT
85.5 x 18.1 x 127.8 mm

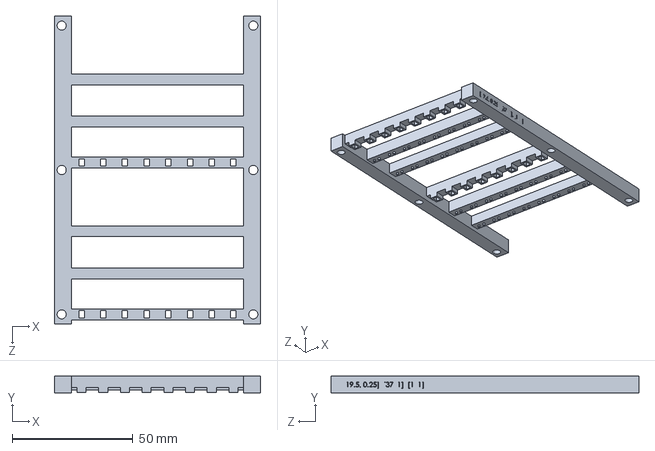
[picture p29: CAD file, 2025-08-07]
hw/CAD models/LFA holders/LFA Holder 3 - top and bottom/v2_strip_holder/strip_tray_v15_bar_doublepoints_wells_flat_bottom_no_bottom_bar_19.5_0.25_37_1_1.SLDPRT
85.5 x 7.00 x 127.8 mm

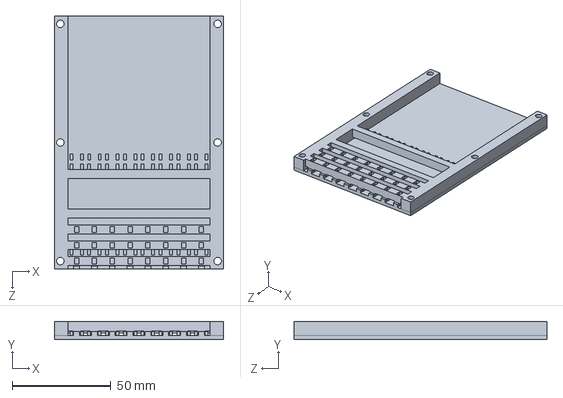
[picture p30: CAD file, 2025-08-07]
hw/CAD models/LFA holders/LFA Holder 3 - top and bottom/v2_strip_holder/strip_tray_v16_1.SLDPRT
85.5 x 9.10 x 127.8 mm

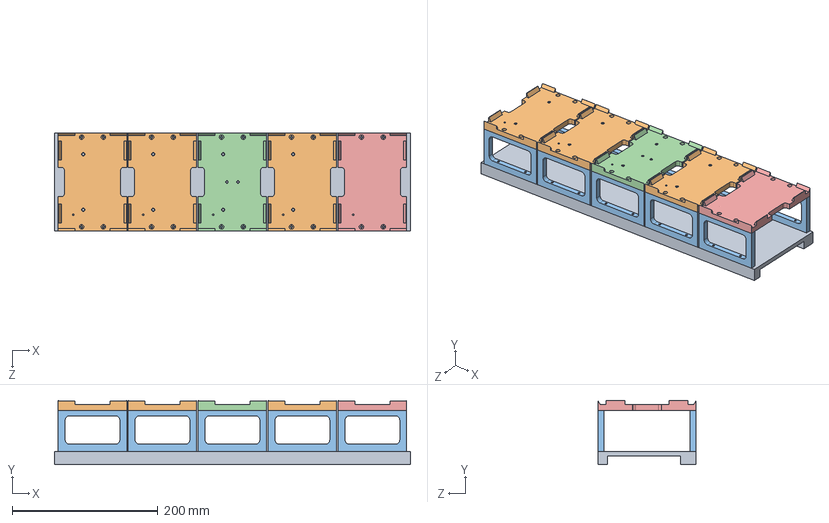
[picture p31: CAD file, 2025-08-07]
hw/CAD models/Custom plates and ancillary pieces/047284.SLDASM
488.3 x 88.4 x 134.0 mm

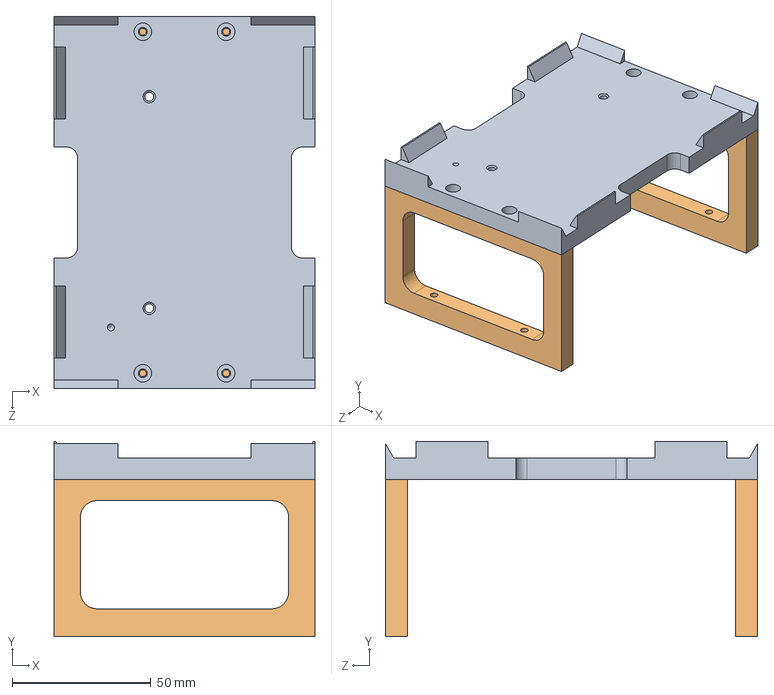
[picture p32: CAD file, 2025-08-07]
hw/CAD models/Custom plates and ancillary pieces/047279.SLDASM
94.0 x 70.3 x 134.0 mm

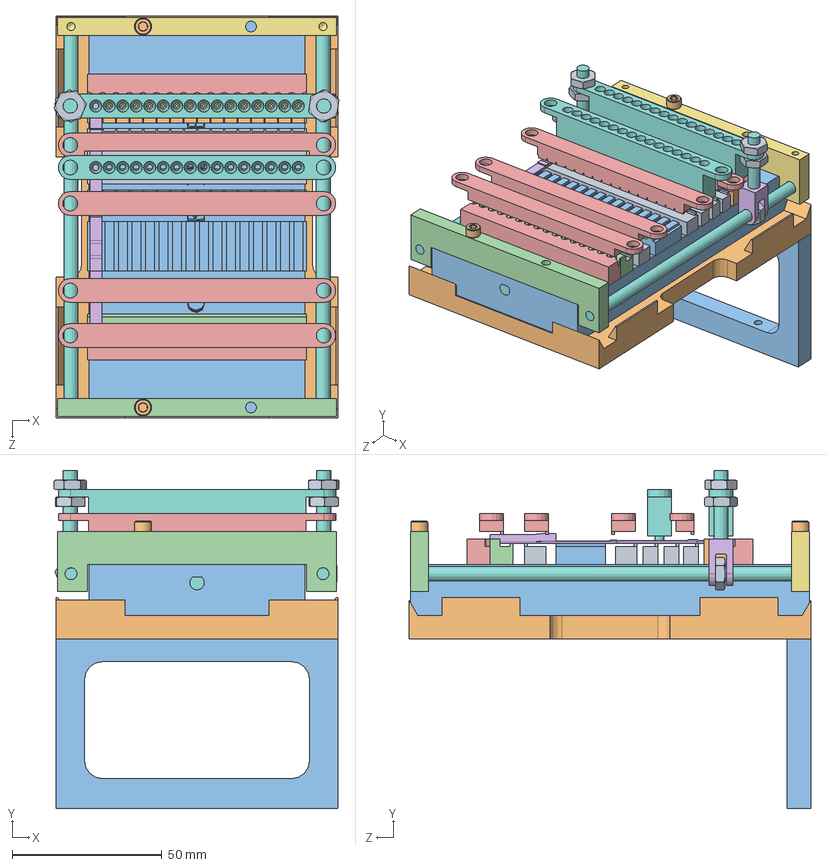
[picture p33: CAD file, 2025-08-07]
hw/CAD models/LFA holders/LFA Holder 1 - Infinite DoF/036639.sldasm
95.0 x 112.7 x 134.0 mm

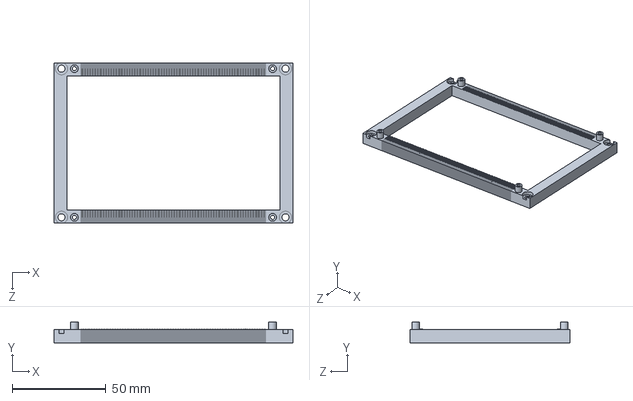
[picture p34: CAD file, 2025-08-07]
hw/CAD models/LFA holders/LFA Holder 2 - Lego approach/041305.SLDASM
127.8 x 11.0 x 85.5 mm

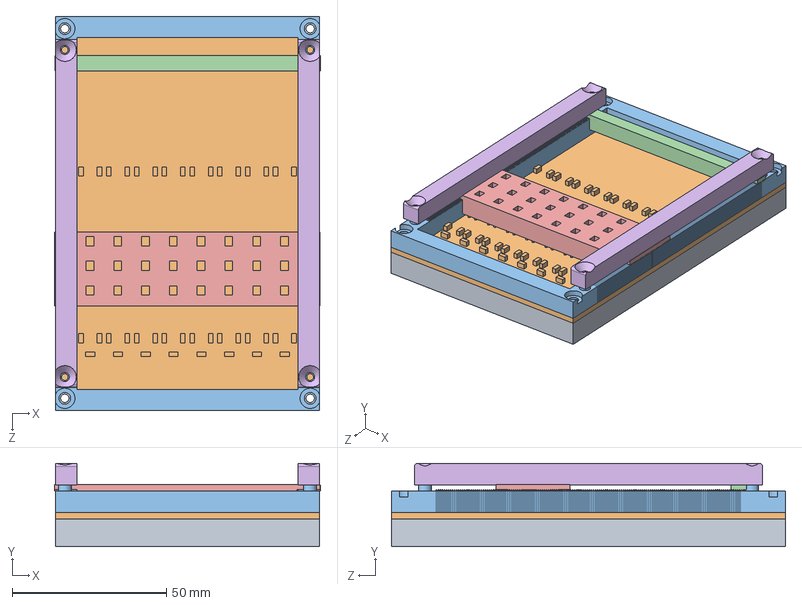
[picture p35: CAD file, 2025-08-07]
hw/CAD models/LFA holders/LFA Holder 2 - Lego approach/042798.sldasm
86.2 x 27.0 x 127.8 mm

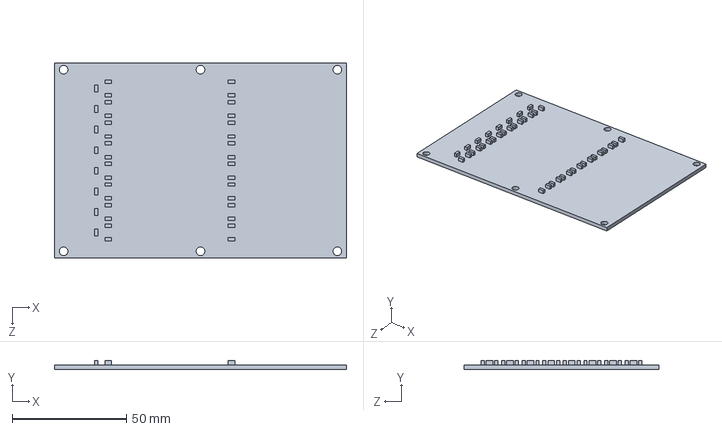
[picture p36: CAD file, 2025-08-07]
hw/CAD models/LFA holders/LFA Holder 2 - Lego approach/042800.sldprt
127.8 x 4.00 x 85.5 mm

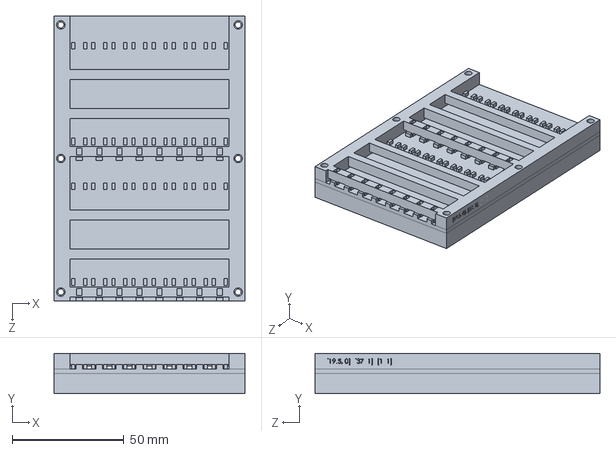
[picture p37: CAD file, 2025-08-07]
hw/CAD models/LFA holders/LFA Holder 3 - top and bottom/056923.SLDPRT
85.5 x 18.1 x 127.8 mm

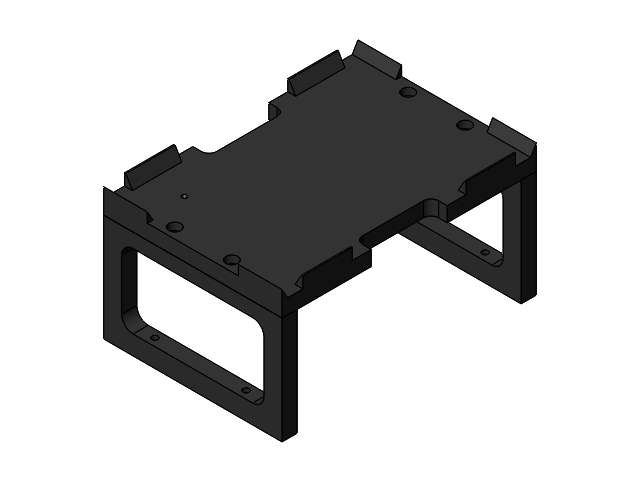
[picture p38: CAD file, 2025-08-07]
hw/CAD models/LFA holders/LFA Holder 1 - Infinite DoF/036642.sldasm


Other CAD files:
hw/CAD models/LFA holders/LFA Holder 3 - top and bottom/v2_strip_holder/Essentials_testpart.SLDPRT
hw/CAD models/Custom plates and ancillary pieces/047281.SLDASM
hw/CAD models/Custom plates and ancillary pieces/047282.SLDASM
hw/CAD models/LFA holders/LFA Holder 1 - Infinite DoF/036661.sldprt
hw/CAD models/Custom plates and ancillary pieces/047273.SLDPRT
hw/CAD models/Custom plates and ancillary pieces/047274.SLDPRT
hw/CAD models/Custom plates and ancillary pieces/047275.SLDPRT
hw/CAD models/Custom plates and ancillary pieces/047277.SLDPRT
hw/CAD models/Custom plates and ancillary pieces/047283.SLDPRT
hw/CAD models/Custom plates and ancillary pieces/047286.SLDPRT
hw/CAD models/Custom plates and ancillary pieces/047287.SLDPRT
hw/CAD models/Custom plates and ancillary pieces/047288.SLDPRT
hw/CAD models/Custom plates and ancillary pieces/047295.SLDPRT
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

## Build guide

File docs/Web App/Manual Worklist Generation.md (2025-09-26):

### Define experiment details 

Specify the number of assay steps, timing delays between steps, reagent types and reagent volumes required for each step. This includes addition of antibodies, addition of sample, addition of running buffer, and LFA imaging. These parameters are used to populate  the following columns in the worklist: ‘step’, ‘volume_ul’, ‘liquid_class’, ‘timer_delta’, ‘source’, ‘step_index’, ‘group_number’, ‘timer_group_check’.

### Determine experiment hardware

Based on the total volume of each reagent type, determine the appropriate hardware plate to hold each reagent, and layout reagents accordingly. Include an additional 30% volume to account for losses during pipetting. Reagents with volumes ≥ 200 uL should be placed in a 96 deep well plate, those with volumes < 200 uL in a 96 well plate, and those with volumes < 100 uL in a 384 well plate. This information is use to populate the ‘from plate’ and ‘from_well’ columns in the worklist .csv file.

Identify the appropriate custom LFA-hardware based on the assay architecture (i.e, LFA strips with or without cassette). Measure and note the precise pipetting and/or imaging locations. This information is used to populate ‘dx’, ‘dz’, ‘to_plate’, and ‘to_well’ columns in the worklist .csv file.

### Prepare worklist 

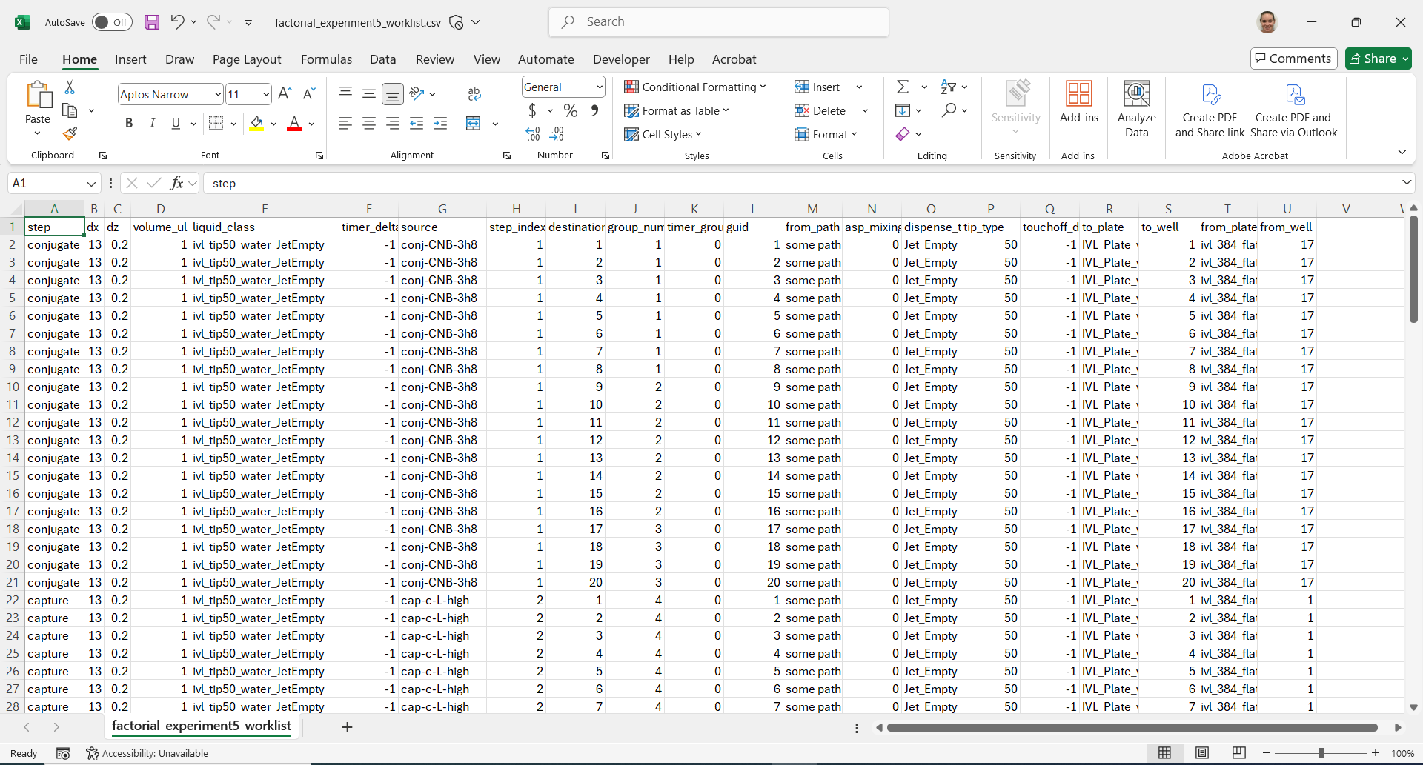
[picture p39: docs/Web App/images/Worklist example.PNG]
Worklist example image
 <br>
<small>Figure 1. Example worklist, with corresponding column headers and each step indicated by a single row. </small>

Generate the "...worklist.csv" file by translating the calculated reagent volumes and plate layouts into line-by-line commands. Ensure that each step is accurately represented in the worklist format. Refer to the definitions provided in the Glossary to confirm that all required information are included in the file.

### Validate worklist 
Test the worklist in simulation mode, closely monitoring the execution of each command to ensure accuracy. Revise and iterate as needed based on observed discrepancies or errors.

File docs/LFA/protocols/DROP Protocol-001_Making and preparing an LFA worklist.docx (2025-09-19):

# 1 Purpose

This document describes how to make a worklist to run an experiment on the Hamilton STAR liquid handling robot. The experimental design described here is specifically for running and/or optimizing lateral flow assays (LFAs).

# 2 Scope

This document applies to the Hamilton STAR liquid handling robot and its operators.

# 3 Definitions

TERM | DEFINITION
PPE | Personal Protective Equipment

# 4 Related Documents

1. Hamilton STAR Operator Manual
2. Microlab STAR Software Programmer Manual
3. DROP SOP-001: Hamilton STAR operation
4. DROP Protocol-002: LFA Image Analysis

# 5 Roles and Responsibilities

Role | Responsibility
Principal User | - Establish and implement this procedure - Ensure users are adequately trained in use of this instrument - Complete Training Form and provide to Quality Manager for recordkeeping - Review procedure periodically for necessary updates
Instrument User | - Complete training on use of the instrument - Perform tasks as specified in procedure
Lab Manager | - Review procedure periodically for necessary updates

# 6 Worklist Background

## 6.1 The worklist is a .csv file that is input into the Hamilton Run Control to the robot what actions to follow and in what order.

## 6.2 The file containing the worklist must end with ‘worklist.csv’ otherwise the Hamilton software will not recognize it. The file containing the worklist must end with worklist.csv; otherwise, the Hamilton software will not recognize it.

## 6.3 The file must be a plain .csv file (not a UTF-8 or any other csv version).

## 6.4 A worklist can be made manually or by coding. For LFA optimization work, we have python-based code called the “Robot Worklist Generator”.

## 6.5 The worklist is composed of 21 columns (two of which are optional) and infinite rows. The identity and definition of each of these columns is described in Section 8. The order of the columns does not matter.

# 7 Worklist Column Definitions

## 7.1 step – a text string to describe what the step is (e.g. conjugate addition, sample addition, buffer addition, imaging)

## 7.2 volume_µL – volume to be pipetted. Must be smaller than the volume associated with the liquid class (50, 300, or 1000 depending). If volume is set to 0, the robot will take a picture instead of pipetting.

7.3 liquid_class – liquid class associated with the liquid to be pipetted. These classes have been designed specifically for the liquids that we pipette and the volumes we plan to use. There is a list of possible liquid classes found in the CO-RE liquid editor. The specific liquid classes designed for LFAs can be found in the LFA documentation.

## 7.4 tip_type – this value is associated with the liquid class selected and the volume to be pipetted. This value will be either 50, 300, or 1000. This value needs to be larger than the volume to be pipetted.

7.5 dispense_type – two dispense types, “Surface_Empty” and “Jet_Empty” are used. Surface_Empty goes to the tip of the liquid, detected using a capacitive measurement, and dispenses 2mm below that height. This feature struggles when there are bubbles at the top of a liquid. Jet_Empty goes inside the well and dispenses at a set height above the bottom of the well plate. Jet_Empty tends to be accurate at faster speeds than Surface Empty.

## 7.6 asp_mixing – programs the number of mixing cycles performed after a dispense step. This value needs to be the same value for an entire group. This feature only works for Surface_Empty liquid classes.

## 7.7 source – the name of the liquid that is being pipetted. By using specific descriptors, source can be useful for the user when designing the worklist.

7.8 group_number – the “group” classification is an important one. Each group needs to be from the same tip_type (50, 300, 1000). The group number is used by the robot to control the order and timing of pipetting steps. It is recommended to keep groups of 8 rows if you want to control the order in which the robot completes each step.

## Note: if one item in a group has mixing step, for example, then all items in that group will be mixed. However, using too many groups will make the method too slow. Therefore, group numbers need to be assigned wisely.

## 7.9 timer_delta – If the assay has time dependent steps, a value to program a time delay between the step and the next (associated) step, defined in timer_group_check. The value here is in seconds.

## 7.10 timer_group_check – this value will tell the program which step from which the time should refer to, in seconds. For example, if you wanted group 3 to occur 10 minutes after group 1 is complete, then your group_number=3, timer_group_check=1, and timer_delta (for group 1) = 600.

## 7.11 touchoff_dis –used to change the distance vertically that the pipette tip moves up after touching a surface before dispensing. Set value to -1 when not in use.

## 7.12 to_plate – the ID of the plate pipetting step is going to. For most cases, there are more than one of each type of plate on the deck, indicated by the number at the end of the to_plate ID. Plates used in LFA applications are the following:

Table 1. Plate IDs with descriptions.

Type of plate | to_plate ID | Max volume per well (practical 80%)
96 well DW plate | dw_96_0001, dw_96_0002, dw_96_003 | 1000 µL (800)
96 well flat bottom plate | flat_96_0001, flat_96_0002, flat_96_0003 | 300 µL (240)
384 well flat bottom plate | flat_384_0001, flat_384_0002, flat_384_0003 | 100 µL (80)
Multichannel reservoir | flat_reservoir_0001, flat_reservoir_0002, flat_reservoir_0003 | 50-100 mL

## Note: Any standard plate will work for each of the categories above.

Table 2. Plate IDs for LFA holders.

Type of custom LFA- hardware | to_plate ID
LFA strip holder | 16 strip holders: 8 x 2 IVL_Plate_v2a_16strips_plastic_col_first_0001 to 012
LFA cassette holder | 96 cassettes: 16 x 6 IVL_Plate_v3_96cassettes_ABformat_0001 80 cassettes: 16 x 5 IVL_Plate_v1_80cassettes_ABformat_0001

## 7.13 to_well –where pipetting step is going to. The ID ranges from 1-96 for 96 well plates, and 1-384 for 384 well plates. Independent of plate size, the numbering is always top to bottom, left to right. Examples of the layout for each plate type are shown below.

96 well plate

96 | 1 | 2 | 3 | 4 | 5 | 6 | 7 | 8 | 9 | 10 | 11 | 12
A | 1 | 9 | 17 | 25 | 33 | 41 | 49 | 57 | 65 | 73 | 81 | 89
B | 2 | 10 | 18 | 26 | 34 | 42 | 50 | 58 | 66 | 74 | 82 | 90
C | 3 | 11 | 19 | 27 | 35 | 43 | 51 | 59 | 67 | 75 | 83 | 91
D | 4 | 12 | 20 | 28 | 36 | 44 | 52 | 60 | 68 | 76 | 84 | 92
E | 5 | 13 | 21 | 29 | 37 | 45 | 53 | 61 | 69 | 77 | 85 | 93
F | 6 | 14 | 22 | 30 | 38 | 46 | 54 | 62 | 70 | 78 | 86 | 94
G | 7 | 15 | 23 | 31 | 39 | 47 | 55 | 63 | 71 | 79 | 87 | 95
H | 8 | 16 | 24 | 32 | 40 | 48 | 56 | 64 | 72 | 80 | 88 | 96

384 well plate

384 | 1 | 2 | 3 | 4 | 5 | 6 | 7 | 8 | 9 | 10 | 11 | 12 | 13 | 14 | 15 | 16 | 17 | 18 | 19 | 20 | 21 | 22 | 23 | 24
A | 1 | 17 | 33 | 49 | 65 | 81 | 97 | 113 | 129 | 145 | 161 | 177 | 193 | 209 | 225 | 241 | 257 | 273 | 289 | 305 | 321 | 337 | 353 | 369
B | 2 | 18 | 34 | 50 | 66 | 82 | 98 | 114 | 130 | 146 | 162 | 178 | 194 | 210 | 226 | 242 | 258 | 274 | 290 | 306 | 322 | 338 | 354 | 370
C | 3 | 19 | 35 | 51 | 67 | 83 | 99 | 115 | 131 | 147 | 163 | 179 | 195 | 211 | 227 | 243 | 259 | 275 | 291 | 307 | 323 | 339 | 355 | 371
D | 4 | 20 | 36 | 52 | 68 | 84 | 100 | 116 | 132 | 148 | 164 | 180 | 196 | 212 | 228 | 244 | 260 | 276 | 292 | 308 | 324 | 340 | 356 | 372
E | 5 | 21 | 37 | 53 | 69 | 85 | 101 | 117 | 133 | 149 | 165 | 181 | 197 | 213 | 229 | 245 | 261 | 277 | 293 | 309 | 325 | 341 | 357 | 373
F | 6 | 22 | 38 | 54 | 70 | 86 | 102 | 118 | 134 | 150 | 166 | 182 | 198 | 214 | 230 | 246 | 262 | 278 | 294 | 310 | 326 | 342 | 358 | 374
G | 7 | 23 | 39 | 55 | 71 | 87 | 103 | 119 | 135 | 151 | 167 | 183 | 199 | 215 | 231 | 247 | 263 | 279 | 295 | 311 | 327 | 343 | 359 | 375
H | 8 | 24 | 40 | 56 | 72 | 88 | 104 | 120 | 136 | 152 | 168 | 184 | 200 | 216 | 232 | 248 | 264 | 280 | 296 | 312 | 328 | 344 | 360 | 376
I | 9 | 25 | 41 | 57 | 73 | 89 | 105 | 121 | 137 | 153 | 169 | 185 | 201 | 217 | 233 | 249 | 265 | 281 | 297 | 313 | 329 | 345 | 361 | 377
J | 10 | 26 | 42 | 58 | 74 | 90 | 106 | 122 | 138 | 154 | 170 | 186 | 202 | 218 | 234 | 250 | 266 | 282 | 298 | 314 | 330 | 346 | 362 | 378
K | 11 | 27 | 43 | 59 | 75 | 91 | 107 | 123 | 139 | 155 | 171 | 187 | 203 | 219 | 235 | 251 | 267 | 283 | 299 | 315 | 331 | 347 | 363 | 379
L | 12 | 28 | 44 | 60 | 76 | 92 | 108 | 124 | 140 | 156 | 172 | 188 | 204 | 220 | 236 | 252 | 268 | 284 | 300 | 316 | 332 | 348 | 364 | 380
M | 13 | 29 | 45 | 61 | 77 | 93 | 109 | 125 | 141 | 157 | 173 | 189 | 205 | 221 | 237 | 253 | 269 | 285 | 301 | 317 | 333 | 349 | 365 | 381
N | 14 | 30 | 46 | 62 | 78 | 94 | 110 | 126 | 142 | 158 | 174 | 190 | 206 | 222 | 238 | 254 | 270 | 286 | 302 | 318 | 334 | 350 | 366 | 382
O | 15 | 31 | 47 | 63 | 79 | 95 | 111 | 127 | 143 | 159 | 175 | 191 | 207 | 223 | 239 | 255 | 271 | 287 | 303 | 319 | 335 | 351 | 367 | 383
P | 16 | 32 | 48 | 64 | 80 | 96 | 112 | 128 | 144 | 160 | 176 | 192 | 208 | 224 | 240 | 256 | 272 | 288 | 304 | 320 | 336 | 352 | 368 | 384

## 7.14 from_plate – plate ID where pipetting step is coming from. See to_plate above for more information about plate IDs.

## 7.15 from_well – well ID where pipetting step is coming from. See to_well above to see more information about well IDs.

## 7.16 step_index –this does not matter. Set value to 0.

## 7.17 destination – this value can be used to name the destination location, which can be useful when making the worklist. Not required by Hamilton software and can be set to default value of 0 if desired.

## 7.18 guid – ID number associated with that specific well or LFA. guid is used for tracking when multiple steps are associated with one assay or assay type.

## 7.19 from_path – string value used to track events. Currently not integrated into workflow. Recommend setting to default value, which is “some path” and use other columns to do so instead.

## 7.20 dx – denotes pipetting location in the x-axis. Origin (0,0) coordinates are hardware dependent, but generally located in the bottom left side of the geometry. Need to be manually verified prior to use.

## 7.21 dz – denotes pipetting location in the z-direction. This value is hardware and instrument dependent. Needs to be manually verified prior to use.

# 8 Making A Worklist

## 8.1 Manual process for making an LFA worklist.

8.1.1 Define the number of assay steps, timing delays between steps, reagent types, reagent volumes required for each step. This includes addition of antibodies, addition of sample, addition of running buffer, and LFA imaging. This information is used to fill out the ‘step’, ‘volume_ul’, ‘liquid_class’, ‘timer_delta’, ‘source’, ‘step_index’, ‘group_number’, ‘timer_group_check’ columns in the worklist.csv file.

8.1.2 Based on the total volume of each reagent type, identify the appropriate hardware plate to hold each reagent, and layout reagents accordingly. Include an additional 30% volume to account for losses during pipetting. Volumes ≥ 200 uL should be placed in a 96 deep well plate, volumes < 200 uL should be placed in a 96 well plate, volumes < 100 uL should be placed in a 384 well plate. This information is use to fill out the ‘from plate’ and ‘from_well’ columns in the worklist .csv file.

8.1.3 Identify the custom LFA-hardware to be used based on the architecture of the RDT (i.e, LFA strips with or without cassette). Measure or note the locations where pipetting needs to take place. This information is used to fill out ‘dx’, ‘dz’, ‘to_plate’, and ‘to_well’ columns in the worklist .csv file.

### 8.1.4 Prepare the worklist. In a “…worklist.csv” file, translate calculations and plate layout into line-by-line commands in the worklist. Use the definitions described in Section 7 to make sure the worklist has all necessary components.

### 8.1.5 Test the worklist in simulation mode. Watch simulation closely to make sure all commands are correct. Iterate as needed.

# 9 Records

This SOP does not generate any records.

# 10 Document Revision History

REV.# | DATE | AFFECTED SECTNS. | CHANGE DESCRIPTION | AUTHOR/OWNER
00 | 01 July 2022 | N/A | (Initial Release) | Caitlin Anderson and Luis Alonzo
01 | 22 October 2024 | 7 | Updated plate names | Caitlin Anderson

Only the four most recent revisions are listed. Archived documents are stored per SOP-0001 Document Control.

<EOF>

CONFIDENTIAL GLOBAL HEALTH LABS Page 2 of 3

CONFIDENTIAL GLOBAL HEALTH LABS Page 2 of 3 Printed on: 20 September 2024

Writing and preparing an LFA worklist 22102024 DROP Protocol-001 Published Date: 10/22/2024

Hamilton STAR Liquid Handling Robot SOP-0042 Rev 00 Owner: Diagnostics Implementation Date: 09 Oct 2020 Last Reviewed Date: 05 Oct 2020

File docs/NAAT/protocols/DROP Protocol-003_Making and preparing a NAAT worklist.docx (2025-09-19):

# 1 Purpose

This document describes how to make a worklist to run an experiment on the Hamilton STAR liquid handling robot. The experimental design described here is specifically for running and/or optimizing nucleic acid amplification tests (NAAT).

# 2 Scope

This document applies to the Hamilton STAR liquid handling robot and its operators.

# 3 Definitions

TERM | DEFINITION
CSV | Comma-separated values file
LFA | Lateral flow assay
MM | Mastermix
NAAT | Nucleic acid amplification test
PPE | Personal Protective Equipment

# 4 Related Documents

1. Hamilton STAR Operator Manual
2. Microlab STAR Software Programmer Manual
3. DROP SOP-001: Hamilton STAR operation
4. DROP Protocol-003: Analyzing NAAT data

# 5 Roles and Responsibilities

Role | Responsibility
Principal User | - Establish and implement this procedure - Ensure users are adequately trained in use of this instrument - Complete Training Form and provide to Quality Manager for recordkeeping - Review procedure periodically for necessary updates
Instrument User | - Complete training on use of the instrument - Perform tasks as specified in procedure
Lab Manager | - Review procedure periodically for necessary updates

# 6 Environmental Health and Safety

Appropriate PPE is required for all Diagnostics Lab activities.

# 7 Worklist Background

## 7.1 The worklist is a .csv file that is input into the Hamilton Run Control to the robot what actions to follow and in what order. The worklist is a *.csv file that is input into the Hamilton Run Control to inform the robot what actions to follow and in what order.

## 7.2 The file containing the worklist must end with worklist.csv otherwise the Hamilton software will not recognize it. The file containing the worklist must end with worklist.csv; otherwise, the Hamilton software will not recognize it.

## 7.3 The file must be a plain .csv file (not a UTF-8 or any other csv version).

## 7.4 A worklist can be made manually or by coding. For LFA optimization work, we have python-based code called the “Robot Worklist Generator”. For NAAT, we are currently developing code with an integrated user interface.

## 7.5 The worklist is composed of 21 columns (two of which are optional) and infinite rows. The identity and definition of each of these columns is described in Section 8. The order of the columns does not matter.

# 8 Worklist Column Definitions

## 8.1 step – a text string to describe what the step is (e.g. make_MM1, mix_MM1, or aliquot_MM1)

## 8.2 volume_µL – volume to be pipetted. Must be smaller than the volume associated with the liquid class (50, 300, or 1000 depending). If volume is set to 0, the robot will take a picture instead of pipetting nothing.

8.3 liquid_class – liquid class associated with the liquid to be pipetted. These classes have been designed specifically for the liquids that we pipette and the volumes we plan to use. There is a list of possible liquid classes found in the CO-RE liquid editor. The specific liquid classes designed for NAAT can be found in the NAAT documentation.

## 8.4 tip_type – this value is associated with the liquid class selected and the volume to be pipetted. This value will be either 50, 300, or 1000. This value needs to be larger than the volume to be pipetted.

8.5 dispense_type – two dispense types, “Surface_Empty” and “Jet_Empty” are used. Surface_Empty goes to the tip of the liquid, detected using a capacitive measurement, and dispenses 2mm below that height. This feature struggles when there are bubbles at the top of a liquid. Jet_Empty goes inside the well and dispenses at a set height above the bottom of the well plate. Jet_Empty tends to be accurate at faster speeds than Surface Empty.

## 8.6 asp_mixing – programs the number of mixing cycles performed after a dispense step. This value needs to be the same value for an entire group. This feature only works for Surface_Empty liquid classes.

## 8.7 source – the name of the liquid that is being pipetted. By using specific descriptors, source can be useful for the user when designing the worklist.

8.8 group_number – the “group” classification is an important one. Each group needs to be from the same tip_type (50, 300, 1000). The group number is used by the robot to control the order and timing of pipetting steps. It is recommended to keep groups of 8 rows if you want to control the order in which the robot completes each step.

## Note: if one item in a group has mixing step, for example, then all items in that group will be mixed. However, using too many groups will make the method too slow. Therefore, group numbers need to be assigned wisely.

8.9 timer_delta – If the assay has time dependent steps, a value to program a time delay between the step and the next (associated) step, defined in timer_group_check. timer_delta – If the assay has time dependent steps, add a value to program a time delay between the step and the next (associated) step, defined in timer_group_check. The value here is in seconds.

## 8.10 timer_group_check – this value will tell the program which step from which the time should refer to, in seconds. For example, if you wanted group 3 to occur 10 minutes after group 1 is complete, then your group_number=3, timer_group_check=1, and timer_delta (for group 1) = 600.

## 8.11 touchoff_dis – this is not currently used for NAAT experiments. Set value to -1. In other applications, this can be used to change the distance vertically that the pipette tip moves up after touching a surface before dispensing.

## 8.12 to_plate – the ID of the plate pipetting step is going to. to_plate – plate ID where the pipetting step is going to. For most cases, there are more than one of each type of plate on the deck, indicated by the number at the end of the to_plate ID. Plates used in NAAT are the following:

Type of plate | to_plate ID | Max volume per well (practical 80%)
96 well DW plate | dw_96_0001, dw_96_0002 | 1000 µL (800)
96 well PCR plate | pcr_96_0001, pcr_96_0002, pcr_96_0003, pcr_96_0004, pcr_96_0005 | 200 µL (160)
96 well flat bottom plate | flat_96_0001, flat_96_0002, flat_96_0003 | 300 µL (240)
384 well PCR plate | pcr_384_0001, pcr_384_0002 | 25 µL (20)
384 well flat bottom plate | None on the current deck design | 100 µL (80)

## Note: Any standard plate will work for each of the categories above. However, if the user intends to use the plate sealer, then the Hamilton specific PCR plates need to be used. Other plates do not have the same material properties and are too stiff to seal correctly.

## 8.13 to_well – well ID where pipetting step is going to. The ID ranges from 1-96 for 96 well plates, and 1-384 for 384 well plates. Independent of plate size, the numbering is always top to bottom, left to right. Examples of the layout for each plate type are shown below.

96 well plate

96 | 1 | 2 | 3 | 4 | 5 | 6 | 7 | 8 | 9 | 10 | 11 | 12
A | 1 | 9 | 17 | 25 | 33 | 41 | 49 | 57 | 65 | 73 | 81 | 89
B | 2 | 10 | 18 | 26 | 34 | 42 | 50 | 58 | 66 | 74 | 82 | 90
C | 3 | 11 | 19 | 27 | 35 | 43 | 51 | 59 | 67 | 75 | 83 | 91
D | 4 | 12 | 20 | 28 | 36 | 44 | 52 | 60 | 68 | 76 | 84 | 92
E | 5 | 13 | 21 | 29 | 37 | 45 | 53 | 61 | 69 | 77 | 85 | 93
F | 6 | 14 | 22 | 30 | 38 | 46 | 54 | 62 | 70 | 78 | 86 | 94
G | 7 | 15 | 23 | 31 | 39 | 47 | 55 | 63 | 71 | 79 | 87 | 95
H | 8 | 16 | 24 | 32 | 40 | 48 | 56 | 64 | 72 | 80 | 88 | 96

384 well plate

384 | 1 | 2 | 3 | 4 | 5 | 6 | 7 | 8 | 9 | 10 | 11 | 12 | 13 | 14 | 15 | 16 | 17 | 18 | 19 | 20 | 21 | 22 | 23 | 24
A | 1 | 17 | 33 | 49 | 65 | 81 | 97 | 113 | 129 | 145 | 161 | 177 | 193 | 209 | 225 | 241 | 257 | 273 | 289 | 305 | 321 | 337 | 353 | 369
B | 2 | 18 | 34 | 50 | 66 | 82 | 98 | 114 | 130 | 146 | 162 | 178 | 194 | 210 | 226 | 242 | 258 | 274 | 290 | 306 | 322 | 338 | 354 | 370
C | 3 | 19 | 35 | 51 | 67 | 83 | 99 | 115 | 131 | 147 | 163 | 179 | 195 | 211 | 227 | 243 | 259 | 275 | 291 | 307 | 323 | 339 | 355 | 371
D | 4 | 20 | 36 | 52 | 68 | 84 | 100 | 116 | 132 | 148 | 164 | 180 | 196 | 212 | 228 | 244 | 260 | 276 | 292 | 308 | 324 | 340 | 356 | 372
E | 5 | 21 | 37 | 53 | 69 | 85 | 101 | 117 | 133 | 149 | 165 | 181 | 197 | 213 | 229 | 245 | 261 | 277 | 293 | 309 | 325 | 341 | 357 | 373
F | 6 | 22 | 38 | 54 | 70 | 86 | 102 | 118 | 134 | 150 | 166 | 182 | 198 | 214 | 230 | 246 | 262 | 278 | 294 | 310 | 326 | 342 | 358 | 374
G | 7 | 23 | 39 | 55 | 71 | 87 | 103 | 119 | 135 | 151 | 167 | 183 | 199 | 215 | 231 | 247 | 263 | 279 | 295 | 311 | 327 | 343 | 359 | 375
H | 8 | 24 | 40 | 56 | 72 | 88 | 104 | 120 | 136 | 152 | 168 | 184 | 200 | 216 | 232 | 248 | 264 | 280 | 296 | 312 | 328 | 344 | 360 | 376
I | 9 | 25 | 41 | 57 | 73 | 89 | 105 | 121 | 137 | 153 | 169 | 185 | 201 | 217 | 233 | 249 | 265 | 281 | 297 | 313 | 329 | 345 | 361 | 377
J | 10 | 26 | 42 | 58 | 74 | 90 | 106 | 122 | 138 | 154 | 170 | 186 | 202 | 218 | 234 | 250 | 266 | 282 | 298 | 314 | 330 | 346 | 362 | 378
K | 11 | 27 | 43 | 59 | 75 | 91 | 107 | 123 | 139 | 155 | 171 | 187 | 203 | 219 | 235 | 251 | 267 | 283 | 299 | 315 | 331 | 347 | 363 | 379
L | 12 | 28 | 44 | 60 | 76 | 92 | 108 | 124 | 140 | 156 | 172 | 188 | 204 | 220 | 236 | 252 | 268 | 284 | 300 | 316 | 332 | 348 | 364 | 380
M | 13 | 29 | 45 | 61 | 77 | 93 | 109 | 125 | 141 | 157 | 173 | 189 | 205 | 221 | 237 | 253 | 269 | 285 | 301 | 317 | 333 | 349 | 365 | 381
N | 14 | 30 | 46 | 62 | 78 | 94 | 110 | 126 | 142 | 158 | 174 | 190 | 206 | 222 | 238 | 254 | 270 | 286 | 302 | 318 | 334 | 350 | 366 | 382
O | 15 | 31 | 47 | 63 | 79 | 95 | 111 | 127 | 143 | 159 | 175 | 191 | 207 | 223 | 239 | 255 | 271 | 287 | 303 | 319 | 335 | 351 | 367 | 383
P | 16 | 32 | 48 | 64 | 80 | 96 | 112 | 128 | 144 | 160 | 176 | 192 | 208 | 224 | 240 | 256 | 272 | 288 | 304 | 320 | 336 | 352 | 368 | 384

## 8.14 from_plate – plate ID where pipetting step is coming from. See to_plate above for more information about plate IDs.

## 8.15 from_well – well ID where the pipetting step is coming from. See to_well above for more information about well IDs.

## 8.16 step_index – this does not apply for this work. Set value to 0.

## 8.17 destination – this value can be used to name the destination location, which can be when making the worklist. Not required by Hamilton software and can be set to default value of 0 if desired.

## 8.18 guid – ID number associated with that specific well or LFA. Guid is used for tracking when multiple steps are associated with one assay or assay type.

## 8.19 from_path – string value used to track events. Currently not integrated into workflow. Recommend setting to default value, which is “some path” and use other columns to do so instead.

## 8.20 dx – does not apply to NAAT in current form but is required for pipetting onto LFAs. Set to 0 for this work.

## 8.21 dz – Same as dx above, but in the Z direction. Set to 0 for this work.

# 9 Making A Worklist

## 9.1 Manual process for making a NAAT worklist.

### 9.1.1 Before making a worklist, calculate the volume of reagents required to make the mastermix. It is recommended to prepare 30% more mastermix volume than is required for the number of replicates to account for dead volume.

9.1.2 Design plate layout. This includes layouts for stock reagent plates and assay plates. Choose reagent plates based on the volume of reagent required, including the additional 30% volume. Volumes ≥200 uL should be placed in a 96 deep well plate, and volumes <200 uL should be placed in a 96 well PCR plate. If another plate type is desired, ensure that the material is non-binding and DNAse/RNAse/pyrogen to minimize potential impacts on the assay.

### 9.1.3 Prepare the worklist. In a “…worklist.csv” file, translate calculations and plate layout into line-by-line commands in the worklist. Use the definitions described in Section 8 to make sure the worklist has all necessary components.

### 9.1.4 Test the worklist in simulation mode. Watch simulation closely to make sure all commands are correct. Iterate as needed.

## 9.2 Using the RADA web application for making a NAAT worklist. This web app is in development to automate the creation of a worklist, with the information provided above in mind, while removing some of the decision making from the user and streamlining the workflow.

### 9.2.1 Load web app by going to this link -

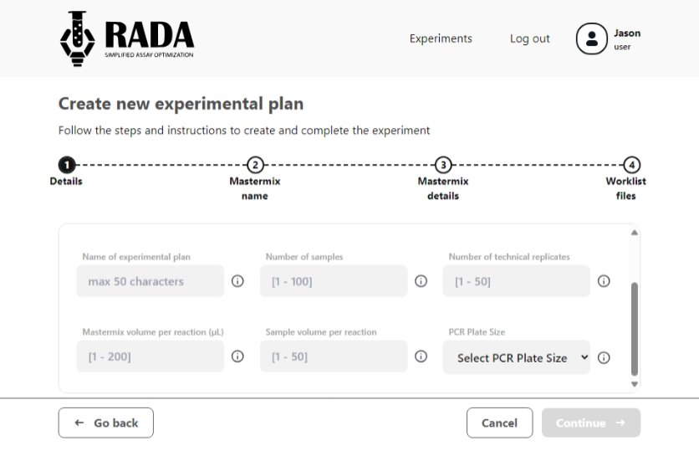
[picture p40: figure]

### 9.2.2 Click “New Experimental Plan” and create a plan. If you have already created an experiment using the app, you can also import an existing experimental plan by selecting “Import existing experimental plan" from the drop-down menu.

### 9.2.3 Fill all sections in the experimental plan details. Additional explanation for each section is included below. Click <Continue> when done.

- Name of experimental plan – text description of experiment (max 50 characters)
- Number of samples – a number, this value needs to include the negative control
- Number of technical replicates – a number, the number of technical replicates required for this experiment
- Mastermix volume per reaction – a number, volume of mastermix only per reaction (not the total reaction volume)
- Sample volume per reaction – a number, the volume of sample per reaction
- PCR plate size – drop down, option of either 96 of 384 well plate size

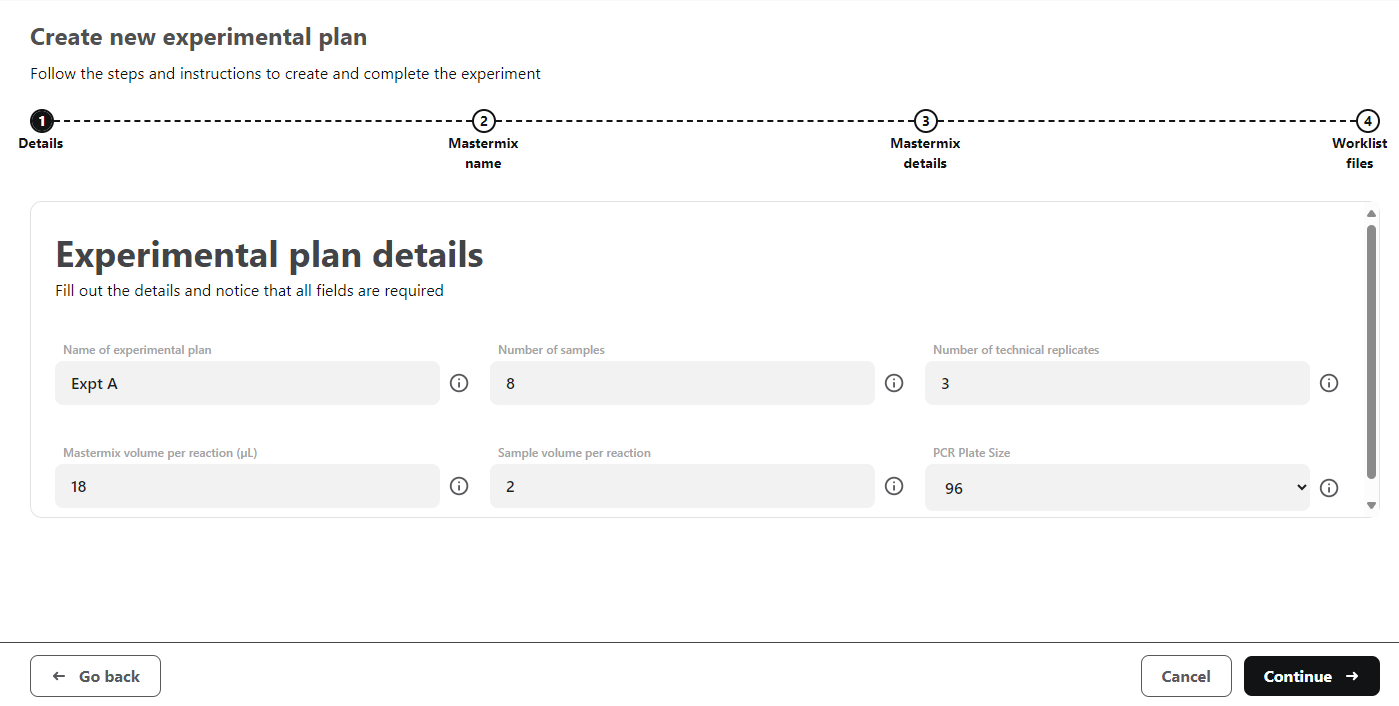
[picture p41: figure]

### 9.2.4 Type in Mastermix name and click <Continue>.

9.2.5 Add mastermix details by entering the values in each column or by selecting values from the drop-down. Load mastermix name in first window, click “Next”. Load mastermix protocol for a mastermix, one reagent at a time. Load reagent, one at a time, to the mastermix as necessary using the “Add reagent” icon. Add them in the order as you would want the robot to prepare the mixture. Each section is described in more detail below.

- Source – the identity of the reagent (i.e. water, buffer, dNTPs, DNA pol, etc)
- Concentration unit – drop down menu with options for concentration value will apply to both the final and stock concentration inputs
- Final and stock concentration – number, must correlate to concentration unit chosen
- Tip washing – Yes/No, select “Yes” if the reagent is viscous (i.e., enzyme in 50% glycerol, dextran, etc)
- Liquid type – drop down menu that correlates with the respective liquid class.
- Dispense type – drop down menu for to select for either Surface_Empty or Jet_Empty. We recommend using “Jet_Empty” for the first reagent in a mastermix (typically water) and “Surface_Empty” for the rest. For more information, refer to definition in Section 8.5

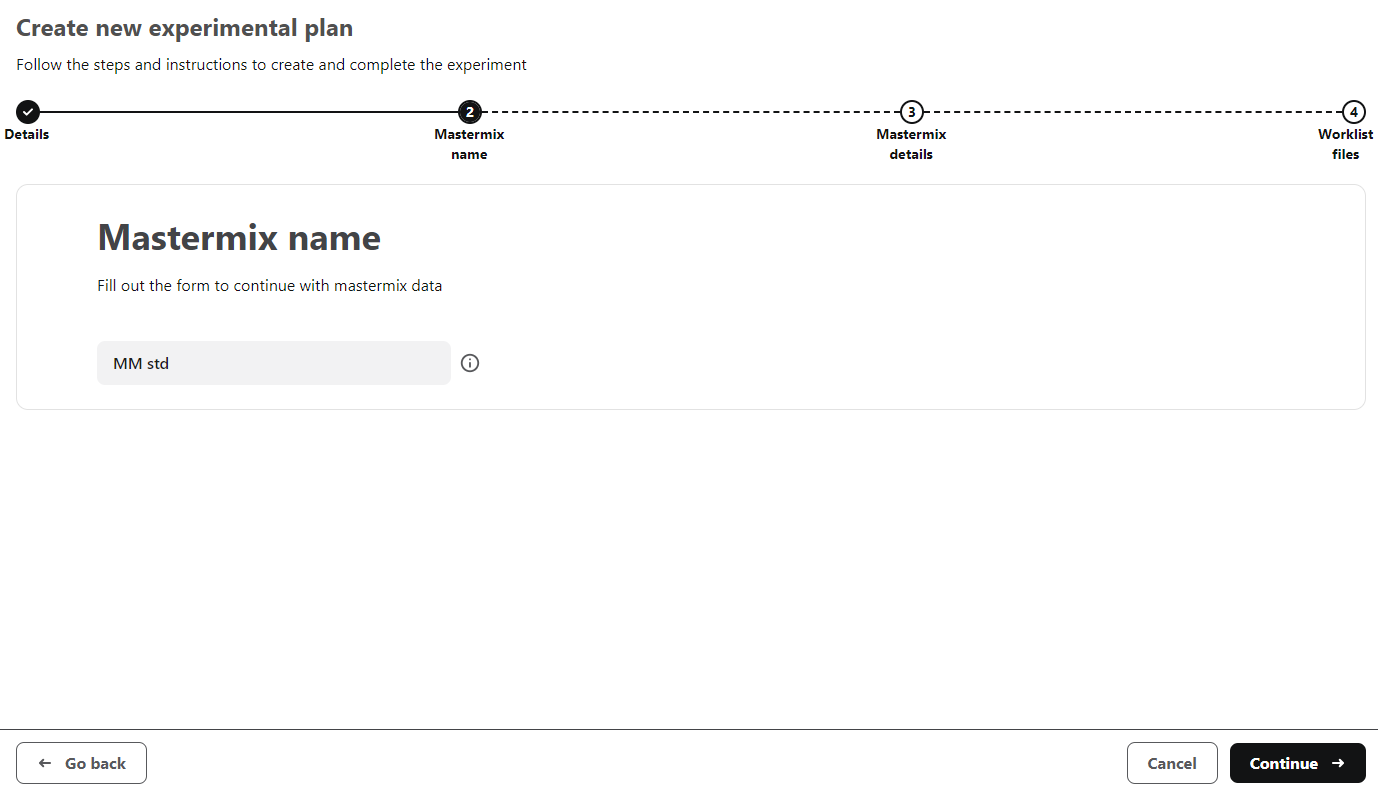
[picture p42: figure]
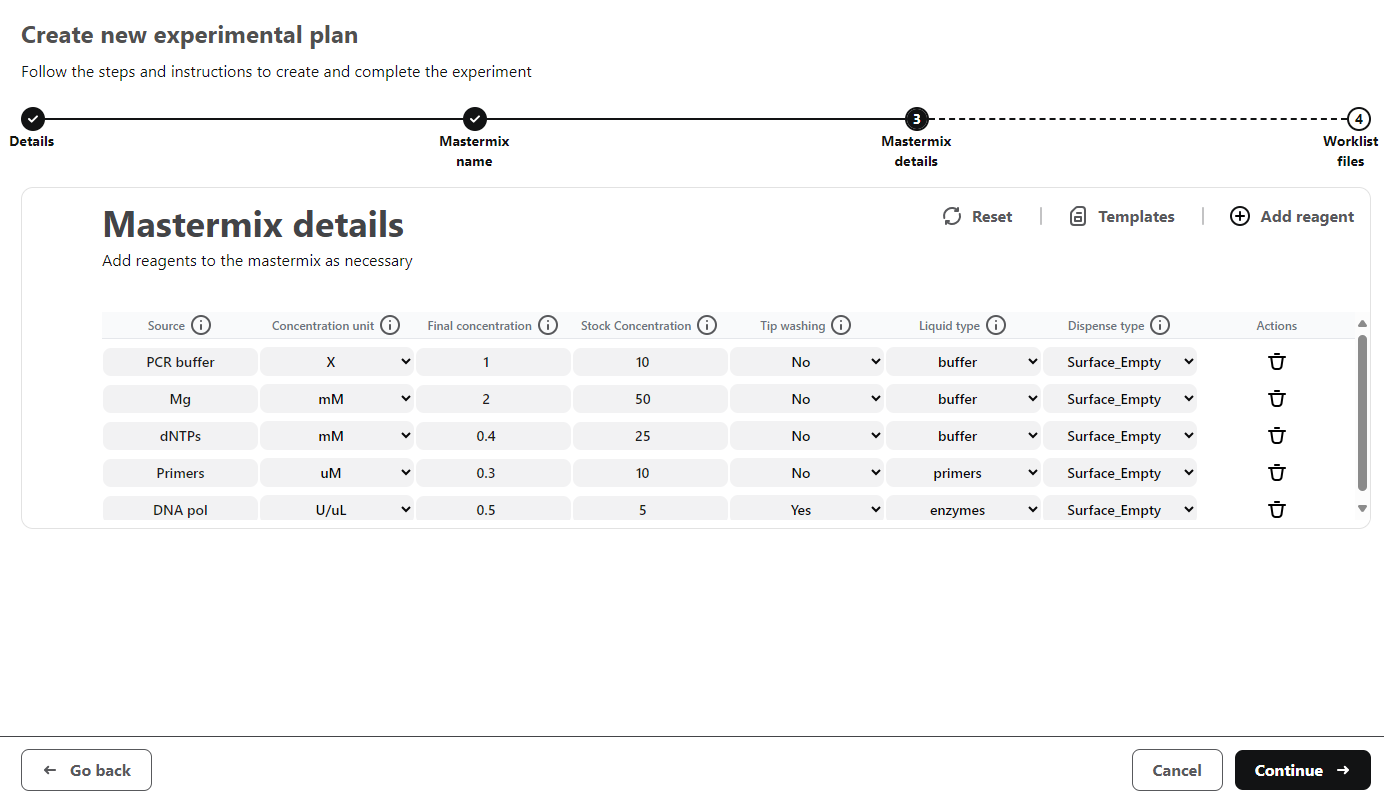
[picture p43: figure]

### 9.2.6 Mastermixes can be copied and/or edited once loaded into the app. To edit, select the pen icon under the “Actions” tab. To copy, select the copy icon. Mastermixes can also be deleted or renamed by clicking the trashcan or dropper icon.

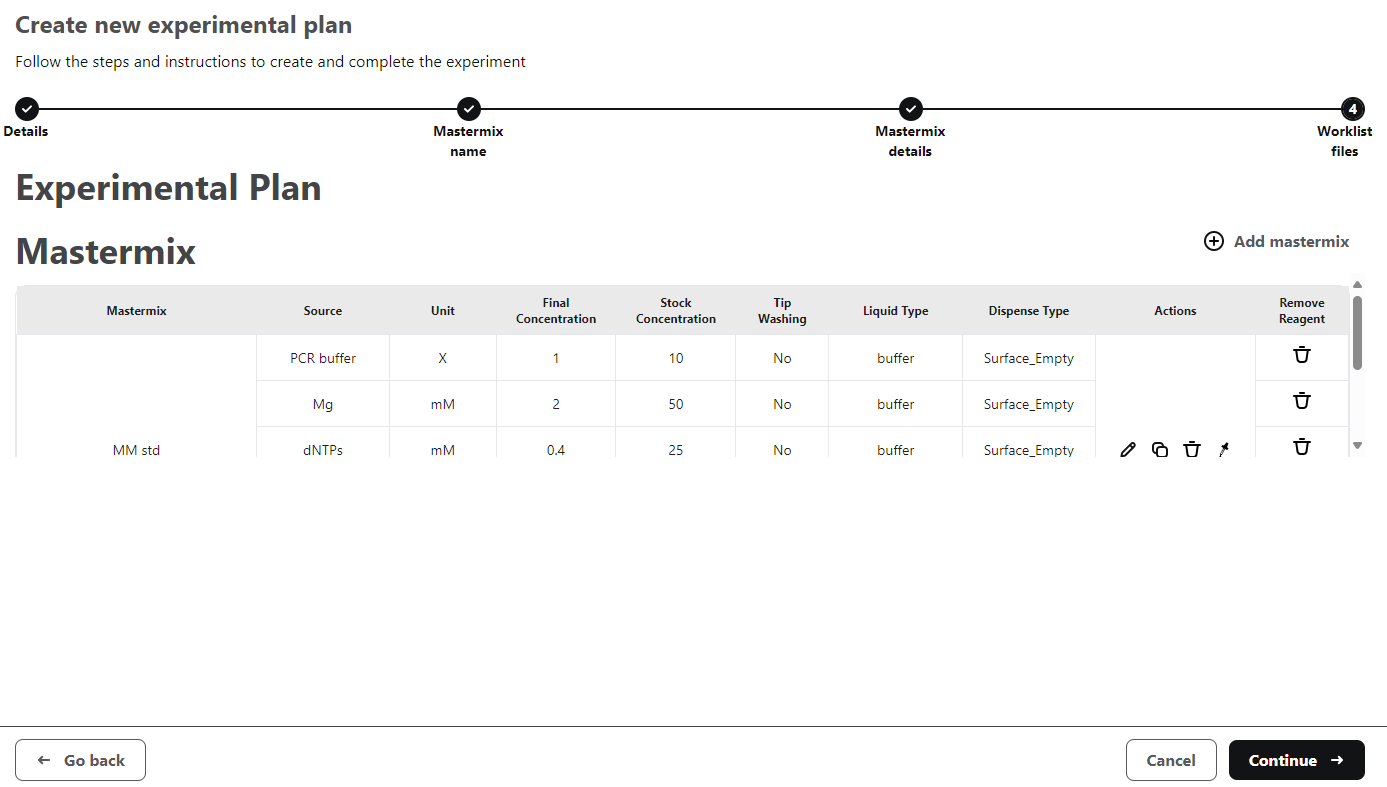
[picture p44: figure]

### 9.2.7 Once the experimental plan and mastermixes are loaded, select “Generate Worklist” to move on to the next step.

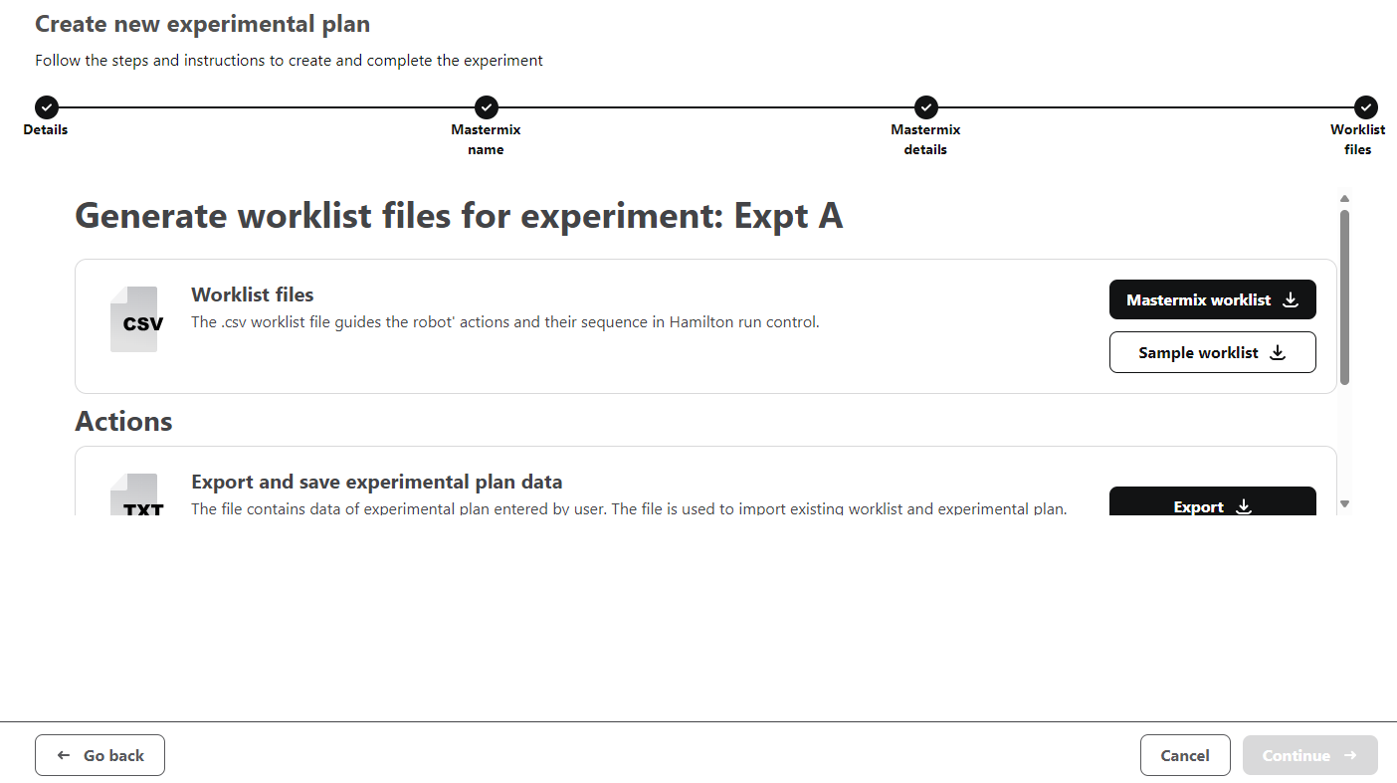
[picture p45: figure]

### 9.2.8 Download mastermix and sample worklists by clicking the “Mastermix worklist” and “Sample worklist” icons. These files are .csv files. Note that the web app output is a CSV UTF-8 (which will not be recognized by the Hamilton software). Before using, make sure to save file as plain .csv file.

### 9.2.9 Download and save experimental data plan by clicking “Export” button. This file is a .txt file and contains all the experimental information to help with one or more of the following:

- Import existing experimental plan to make edits for a new experiment
- Import existing experimental plan to use the worklist viewer when setting up an experiment

DO NOT make edits to this file. Changes in the format of this file will render this file unusable by the app.

### 9.2.10 Load interactive Worklist Viewer by selecting “View Experimental Plan”. You can also load a different (previously exported) experimental plan once in the Worklist Viewer if desired.

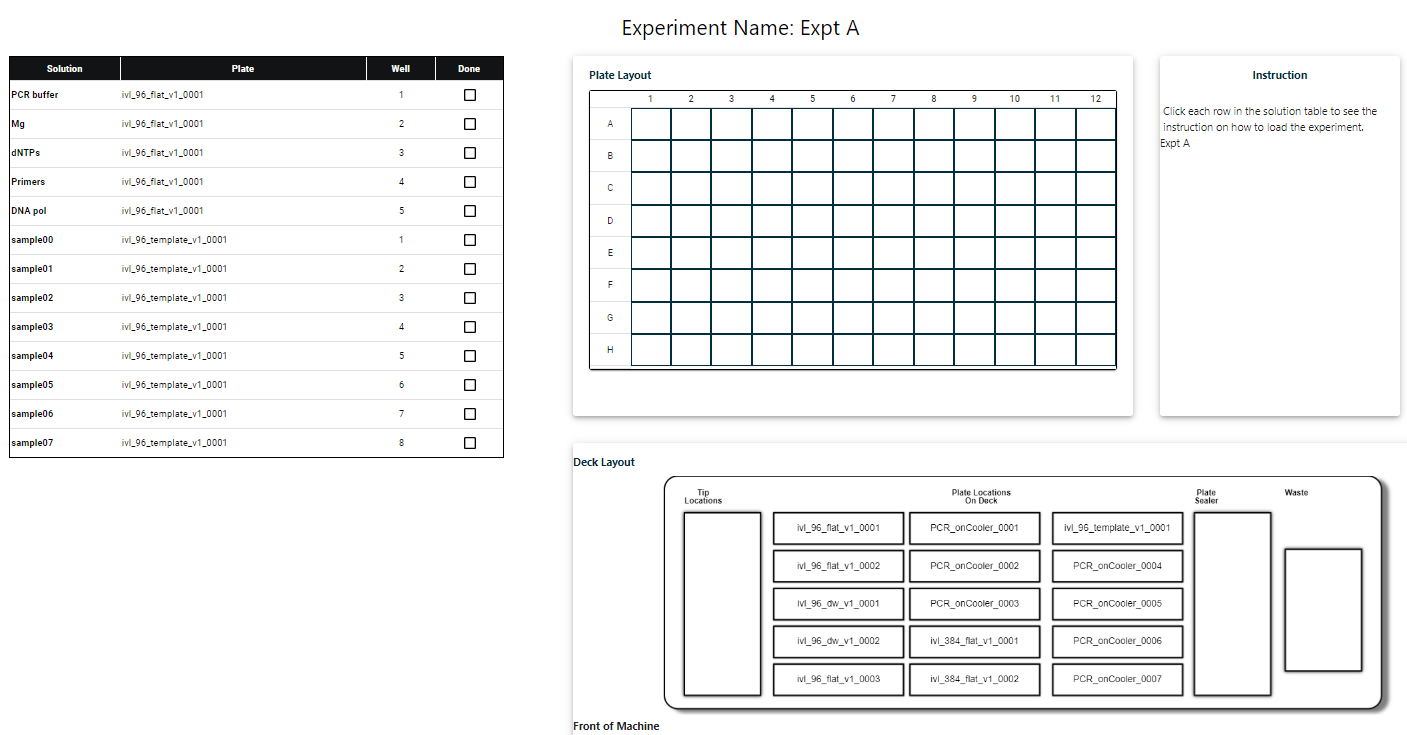
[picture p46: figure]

The worklist viewer has five sections:

1. Reagent loading section – This section includes the list of reagents to be added to run the experiment. It includes solution name (based on user input), plate name, well number, and a check box to indicate when a reagent has been loaded. Click on a given row to highlight locations in the plate layout and deck layout.
2. Plate Layout – Shows the layout of a given plate, 96 or 384. When a given reagent is highlighted, the corresponding well will be highlighted in black.
3. Deck Layout – Shows the layout of the deck, with the corresponding plate names used by the robot to identify plate locations. Similar to the plate layout, the plate corresponding to a specific reagent will be highlighted in black when that reagent is selected.
4. Instructions – When one row in the solution section is selected, instructions will include the solution name, the volume to be pipetted, and the well and plate ID. This can be used by the user to know what to load where, and in what volume.

# 10 Records

This SOP does not generate any records.

# 11 Document Revision History

REV.# | DATE | AFFECTED SECTNS. | CHANGE DESCRIPTION | AUTHOR/OWNER
00 | 01 July 2022 | N/A | (Initial Release) | Caitlin Anderson
01 | 5 October 2022 | Section 9 | Section has been updated to include instructions on using the RoboNAAT Worklist Generator Web App. | Caitlin Anderson
02 | 16 September 2024 | All | Update for new software | Jason Cantera

Only the four most recent revisions are listed.

<EOF>

CONFIDENTIAL GLOBAL HEALTH LABS Page 2 of 3

CONFIDENTIAL GLOBAL HEALTH LABS Page 2 of 3 Printed on: 18 September 2024

Writing and preparing a NAAT worklist REV16092024 DROP Protocol-003 Published Date: 9/16/2024

Hamilton STAR Liquid Handling Robot SOP-0042 Rev 00 Owner: Diagnostics Implementation Date: 09 Oct 2020 Last Reviewed Date: 05 Oct 2020

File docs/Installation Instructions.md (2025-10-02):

## Preparing for installation
1.	Installation requirements for simulation only: 
    - Windows OS (DROP has not been verified with Mac OS)
    - Admin access
    - .NET framework 3.5 or higher. If not already installed on your machine, download from Microsoft here - [link](https://www.microsoft.com/en-us/download/details.aspx?id=21)
    - Microsoft excel or other software that can open and edit .csv files 
2.	Installation requirements for connection to Hamilton STAR 
    - Refer to Hamilton Robotics or local Hamilton distributor 

## Files required for installation 

- DROP Method and Layout Files 
    - :material-folder-download: [DROP LFA Package File (contains Method and Layout file)](https://github.com/Global-Health-Labs/DROP/blob/main/sw/Hamilton%20Files/DROP_NAAT_v2.pkg)
    - :material-folder-download: [DROP LFA Package File (contains Method and Layout file)](https://github.com/Global-Health-Labs/DROP/blob/main/sw/Hamilton%20Files/DROP_LFA_v2.pkg)
- :material-folder-download: [DROP Liquid Classes](https://github.com/Global-Health-Labs/DROP/blob/main/sw/Hamilton%20Files/DROP_Liquid_Classes.mdb) 
- Test Worklists 
    - :fontawesome-solid-file-csv: [Test Mastermix Worklist](https://github.com/Global-Health-Labs/DROP/blob/main/examples/Test%20Worklists/Test_mastermix_worklist.csv) 
    - :fontawesome-solid-file-csv: [Test sample worklist](https://github.com/Global-Health-Labs/DROP/blob/main/examples/Test%20Worklists/Test_sample_worklist.csv)
    - :fontawesome-solid-file-csv: [Test LFA cartridge worklist](https://github.com/Global-Health-Labs/DROP/blob/main/examples/Test%20Worklists/Test_LFA_cassette_worklist.csv) 
    - :fontawesome-solid-file-csv: [Test LFA strip worklist](https://github.com/Global-Health-Labs/DROP/blob/main/examples/Test%20Worklists/Test_LFA_strip_worklist.csv)
- Support packages
    - :material-folder-download: [Shortcuts Import](https://github.com/Global-Health-Labs/DROP/blob/main/sw/Hamilton%20Files/VENUS-Export.zip)
    - :material-folder-download: [EasyPickII Library](https://github.com/Global-Health-Labs/DROP/tree/main/sw/Hamilton%20Files/easyPickIIApplication)

## VENUS installation
1.	Download VENUS onto local machine. Also download the following supporting files that are required as described above.
2.	Run Venus.STAR.Installer.exe and follow the prompts. This step might take a while.
    - When you get to the "Select Features" window, make sure to select ALL features listed. If you skip this step, the final software will not be able to run the Method correctly. <br> <br>
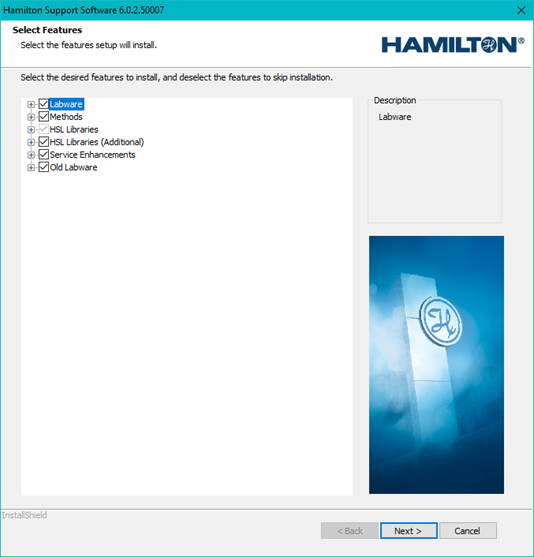
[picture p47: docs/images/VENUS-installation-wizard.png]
VENUS Installation Wizard
     <br>
    <small>Figure 1. Screenshot of VENUS software installation wizard. Select all features to ensure proper execution of the Method. </small> <br><br>
3.	Once installation is completed, open the VENUS software. 

## Method and Library Import 
4.	Navigate to System Tools and click on Hamilton Method Editor. 
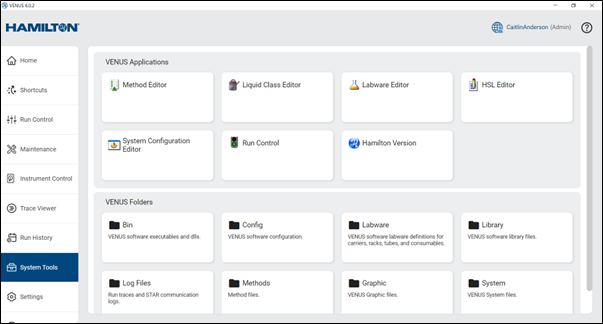
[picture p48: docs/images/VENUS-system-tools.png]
VENUS System Tools
     <br>
    <small> Figure 2. User view of System Tools. Important locations to note for installation are the Method Editor and Liquid Class Editor in the top row. </small> <br><br>
5.	Load following package files one at a time. Make sure they are saved locally onto the machine. 
    - DROP_NAAT.pkg
    - DROP_LFA.pkg
    - STAR_Animations V1.6.0 200416.pkg 
6.	Select "Import" in the Hamilton Method Editor. Make sure to select Import Method/Library/Workflow. Select the "..." and navigate to the .pkg file you are installing. Select "Next". <br> <br>
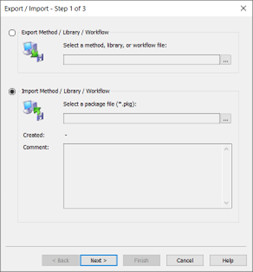
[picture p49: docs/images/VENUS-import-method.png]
VENUS System Tools
     <br>
    <small> Figure 3. Pop up in Hamilton Method Editor to Import a Method file. Make sure that Import Method / Library / Workflow are selected. </small> <br><br>
7.	Select "Import into Default Directories". Once selected, click "Next". <br><br>
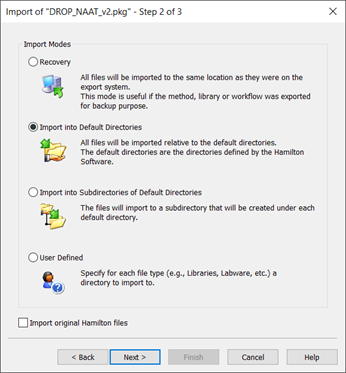
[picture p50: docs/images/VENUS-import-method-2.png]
VENUS System Tools
     <br>
    <small> Figure 4. Instructions for importing a new Method into the Hamilton Method editor. It is recommended to select "Import into Default Directories" as the best option. </small> <br><br>
8.	The package file will be imported. There might be a popup that says that the file already exists and that the existing file is newer than the file in the package. If you get this pop up, select the option "No to all". <br><br>
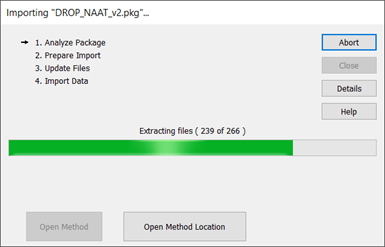
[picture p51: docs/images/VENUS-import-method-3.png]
VENUS System Tools
     <br>
    <small> Figure 5. Screen while the Method is being imported by the Method Editor. </small> <br><br>
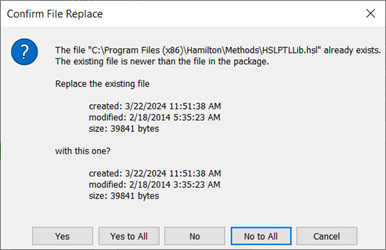
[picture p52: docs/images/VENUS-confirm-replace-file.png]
VENUS confirm replace file
     <br>
    <small> Figure 6. Pop up that may occur when importing a Method in the Method Editor. It is recommended to select "no to all" if the existing file is newer than the file in the package. </small> <br><br>
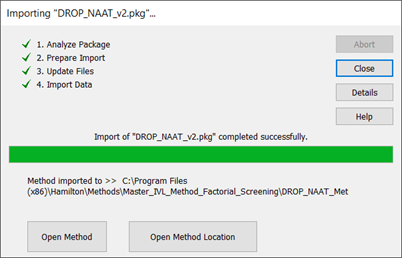
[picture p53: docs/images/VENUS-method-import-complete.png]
VENUS method import complete
     <br>
    <small> Figure 7. Completed import of a Method in the Method Editor. </small> <br><br>

9.	Repeat steps 6-8 for all three package files that need to be imported.
10.	Install easyPickII Application. Ensure that the version of the easyPickII Application is V1.3.2 or newer. This application is required for the function of the camera. 
    - Navigate to the easyPickII Application folder and double click on easypickii.exe.
    - Follow the instructions to install the application.

## Import Liquid Classes
11.	To load the liquid classes required to run the DROP system, navigate back to System Tools in the VENUS software. In System Tools, select the Liquid Class Editor. <br><br>
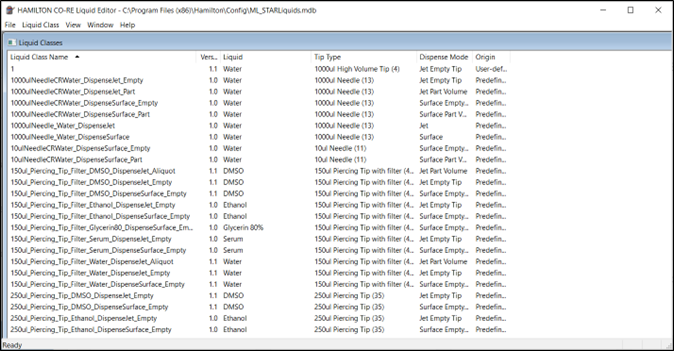
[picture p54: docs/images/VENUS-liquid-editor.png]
Hamilton CO-RE Liquid Editor
     <br>
    <small> Figure 8. View of the Hamilton CO-RE Liquid Editor. This contains all the liquid classes that are imported as well as all default Hamilton liquid classes. </small> <br><br>
12.	Under "File", select "Import Liquid Classes". <br><br>
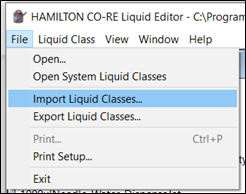
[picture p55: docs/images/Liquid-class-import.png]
Import Liquid Classes
     <br>
    <small> Figure 9. User view in the Liquid class editor to import liquid classes.  </small> <br><br>
13.	Select the file DROP_Liquid_Classes.mdb when prompted to Open File. The liquid classes in the file will load on the left hand side under "Available liquid classes". Select "Add all" to move them into the "Selected liquid classes" column. Then select "OK".<br><br>
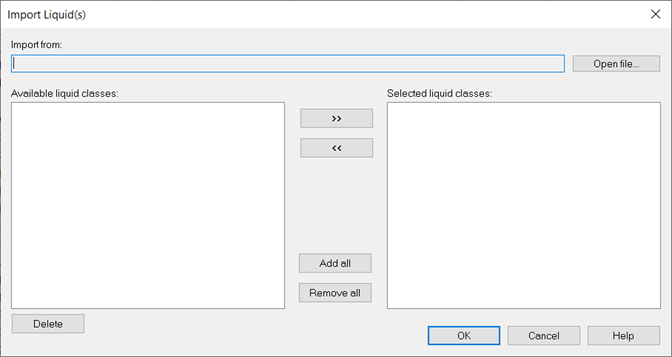
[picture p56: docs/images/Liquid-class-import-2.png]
Import Liquid Classes
     <br>
    <small> Figure 10. User view of the liquid class import page at the start. </small> <br><br>

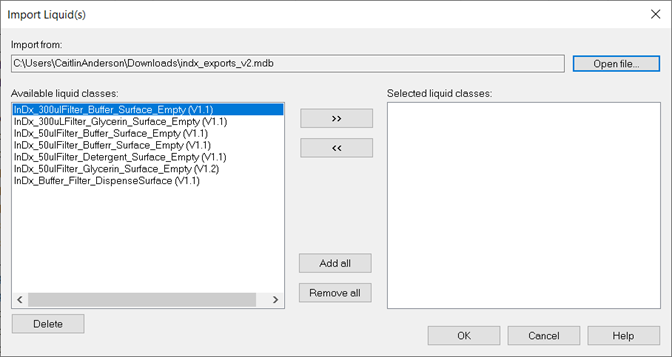
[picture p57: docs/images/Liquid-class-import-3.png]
Import Liquid Classes
     <br>
    <small> Figure 11. User view of the liquid class import page once the .mdb file has been loaded into the "Import from" bar. </small> <br><br>

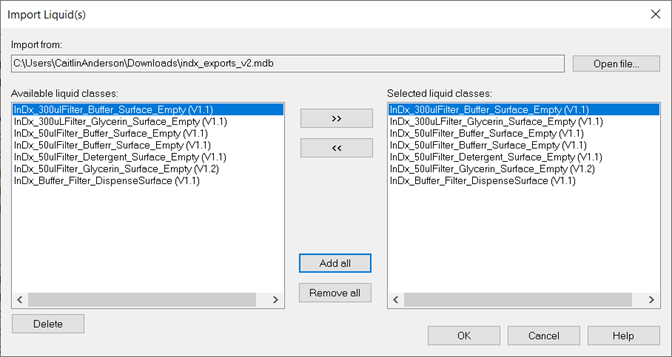
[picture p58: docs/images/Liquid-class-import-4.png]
Import Liquid Classes
     <br>
    <small> Figure 12. User view of the liquid class import page once all of the liquid classes have been selected to be imported. </small> <br><br>
     
14.	Once complete, the new liquid classes can be found in the list of Liquid classes. Verify that is the case and close the Hamilton CO-RE Liquid Editor.  

## Import shortcuts 
15.	Import the shortcuts by navigating to the Settings in the VENUS 6 software. Select the "Shortcuts" tab on the upper bar. Select the three lines on the far right. <br><br>

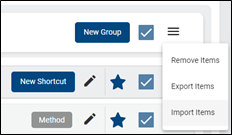
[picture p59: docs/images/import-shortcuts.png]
Import Shortcuts
     <br>
    <small> Figure 13. User view to import shortcuts into VENUS 6. </small> <br><br>

16.	Select Import Items and load the VENUS-Export-Shortcuts.zip file. Once loaded, all of the shortcuts will show up in their respective groupings. Select "Import" and the software will begin importing the selected package(s). <br><br>

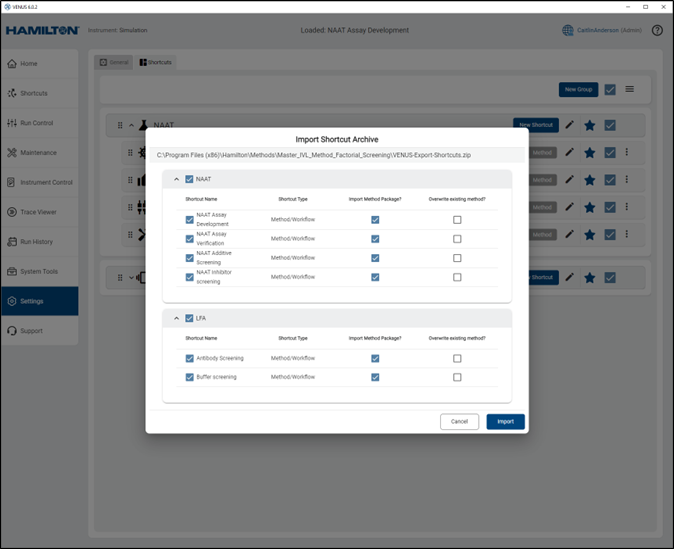
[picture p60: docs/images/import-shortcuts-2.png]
Import Shortcuts
     <br>
    <small> Figure 14. User view when shortcuts have been loaded for import. </small> <br><br>

17.	Once completed, a pop up window will appear stating "Import Shortcut Complete" with the number of successful imports. 

## Testing installation
1.  To test that the installation was successful, open the VENUS Software. 
2.	Navigate to the Shortcuts bar on the Home page. Select the "..." to the right of the "NAAT Assay Development" Shortcut. 
3.	Select "Simulate Method".
4.	Load one of the test worklists into the pop up. Keep "Animation" selected. Click "ok". 
    - For this test use Test_mastermix_worklist.csv
5.	Load tips onto the virtual deck.
6.	Allow the method to run. Take note of any errors that happen. You can refer to the "Common Errors" tab for assistance.

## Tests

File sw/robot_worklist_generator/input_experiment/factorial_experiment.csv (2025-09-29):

step | dx | dz | volume | liquid_class | time | source
Conjugate addition | 13 | 0.2 | 2 | pbst | -1 | conjugate_1,conjugate_2
sample | 0 | 1 | 75 | water | 600 | Pos, Neg
imaging | 24 | 0 | 0 | imaging | 1500 | imaging

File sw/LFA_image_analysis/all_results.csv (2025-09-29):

filename | signal_0 | signal_1 | group | guid
1_20210226_184536.png | 5.917227109021383 | 51.86416008597306 | exp3_full_worklist | 1
2_20210226_184538.png | 63.33630621929933 | 45.78571434415303 | exp3_full_worklist | 2
3_20210226_184539.png | 2.200410509623344 | 42.77117580146669 | exp3_full_worklist | 3
4_20210226_184541.png | 35.1729477823848 | 44.3612977134703 | exp3_full_worklist | 4
5_20210226_184543.png | 2.0473989318078574 | 48.25762223731172 | exp3_full_worklist | 5
6_20210226_184545.png | 48.59175467066118 | 48.71202711484184 | exp3_full_worklist | 6
7_20210226_184546.png | 20.41548548523557 | 52.40991886273719 | exp3_full_worklist | 7
8_20210226_184548.png | 55.1578186660009 | 47.423403375944105 | exp3_full_worklist | 8
9_20210226_184612.png | 2.88828194565805 | 37.89784332156812 | exp3_full_worklist | 9
10_20210226_184614.png | 18.48856463103972 | 42.137171919664425 | exp3_full_worklist | 10
11_20210226_184616.png | 2.33770783690943 | 44.49891313862829 | exp3_full_worklist | 11
12_20210226_184617.png | 18.28656876035216 | 48.48885353230554 | exp3_full_worklist | 12
13_20210226_184619.png | 16.028840602108588 | 47.91299787686328 | exp3_full_worklist | 13
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

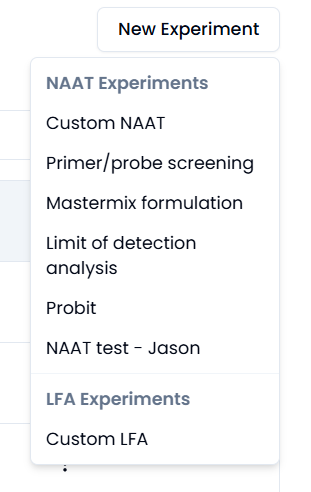
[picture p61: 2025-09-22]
docs/Web App/images/RADA_new_experiment.PNG

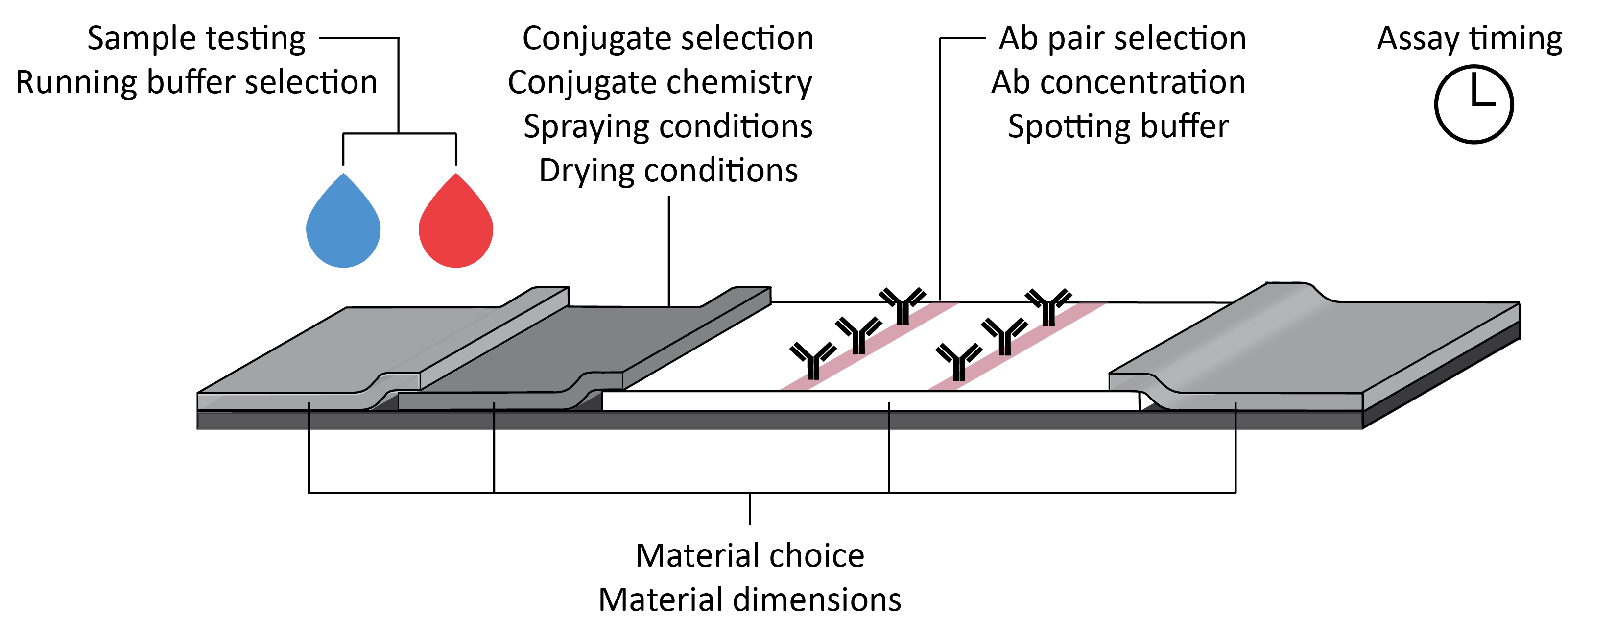
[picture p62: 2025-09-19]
docs/LFA/images/LFA experimental design.png

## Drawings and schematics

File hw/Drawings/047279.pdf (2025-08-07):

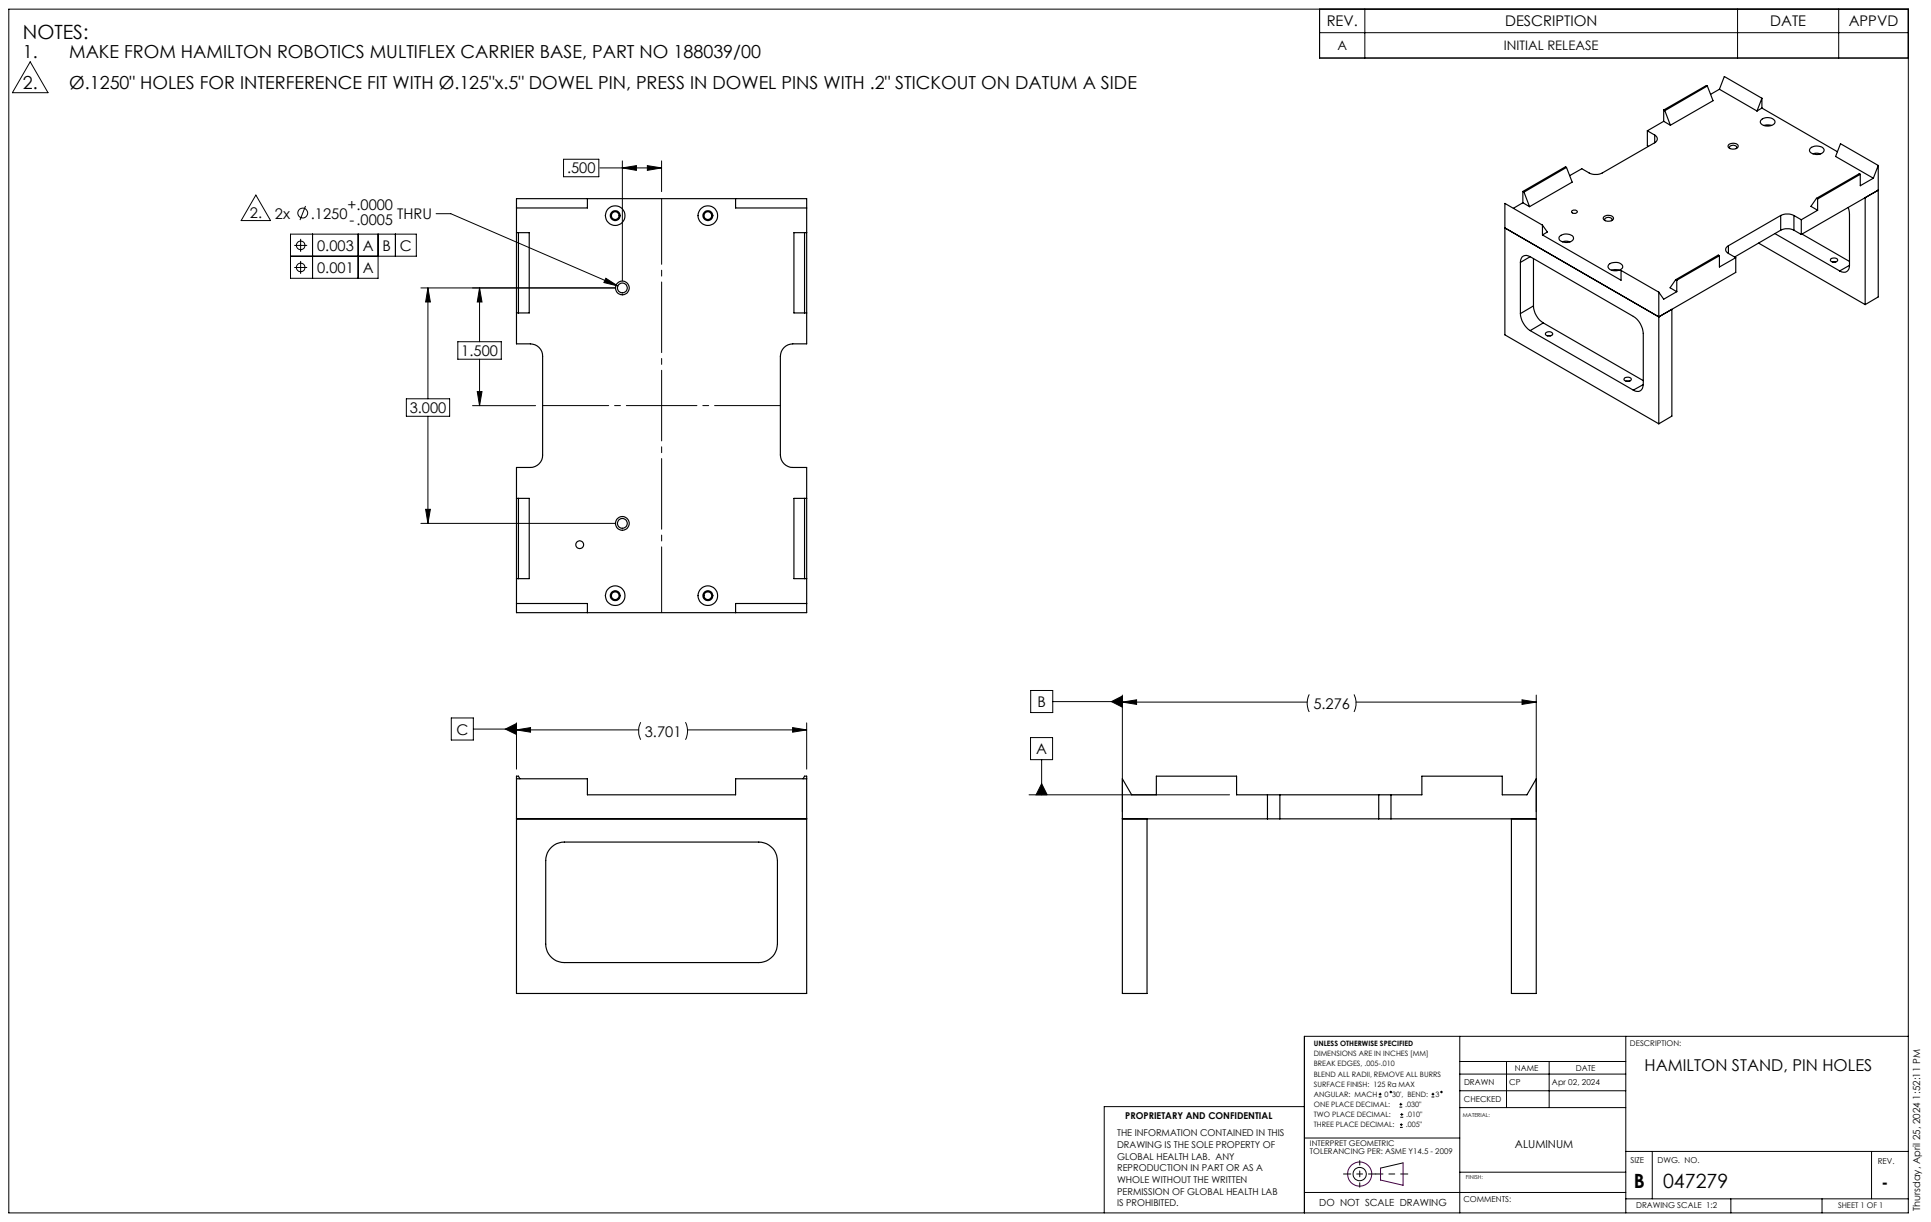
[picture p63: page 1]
.0005 THRU; SHEET 1 OF 1; DO NOT SCALE DRAWING; COMMENTS:; DRAWING SCALE 1:2; DWG. NO.; Apr 02, 2024; ONE PLACE DECIMAL:; TWO PLACE DECIMAL:

NOTES:
1. MAKE FROM HAMILTON ROBOTICS MULTIFLEX CARRIER BASE, PART NO 188039/00
2. Ø.1250" HOLES FOR INTERFERENCE FIT WITH Ø.125"x.5" DOWEL PIN, PRESS IN DOWEL PINS WITH .2" STICKOUT ON DATUM A SIDE

REV. | DESCRIPTION | DATE | APPVD
A | INITIAL RELEASE

UNLESS OTHERWISE SPECIFIED
DIMENSIONS ARE IN INCHES [MM]
BREAK EDGES, .005-.010
BLEND ALL RADII, REMOVE ALL BURRS
SURFACE FINISH: 125 Ra MAX
ANGULAR: MACH 0 30', BEND: 3
THREE PLACE DECIMAL: .005"
INTERPRET GEOMETRIC
TOLERANCING PER: ASME Y14.5 - 2009

DESCRIPTION:
HAMILTON STAND, PIN HOLES

Thursday, April 25, 2024 1:52:11 PM

PROPRIETARY AND CONFIDENTIAL
THE INFORMATION CONTAINED IN THIS
DRAWING IS THE SOLE PROPERTY OF
GLOBAL HEALTH LAB. ANY
REPRODUCTION IN PART OR AS A
WHOLE WITHOUT THE WRITTEN
PERMISSION OF GLOBAL HEALTH LAB
IS PROHIBITED.

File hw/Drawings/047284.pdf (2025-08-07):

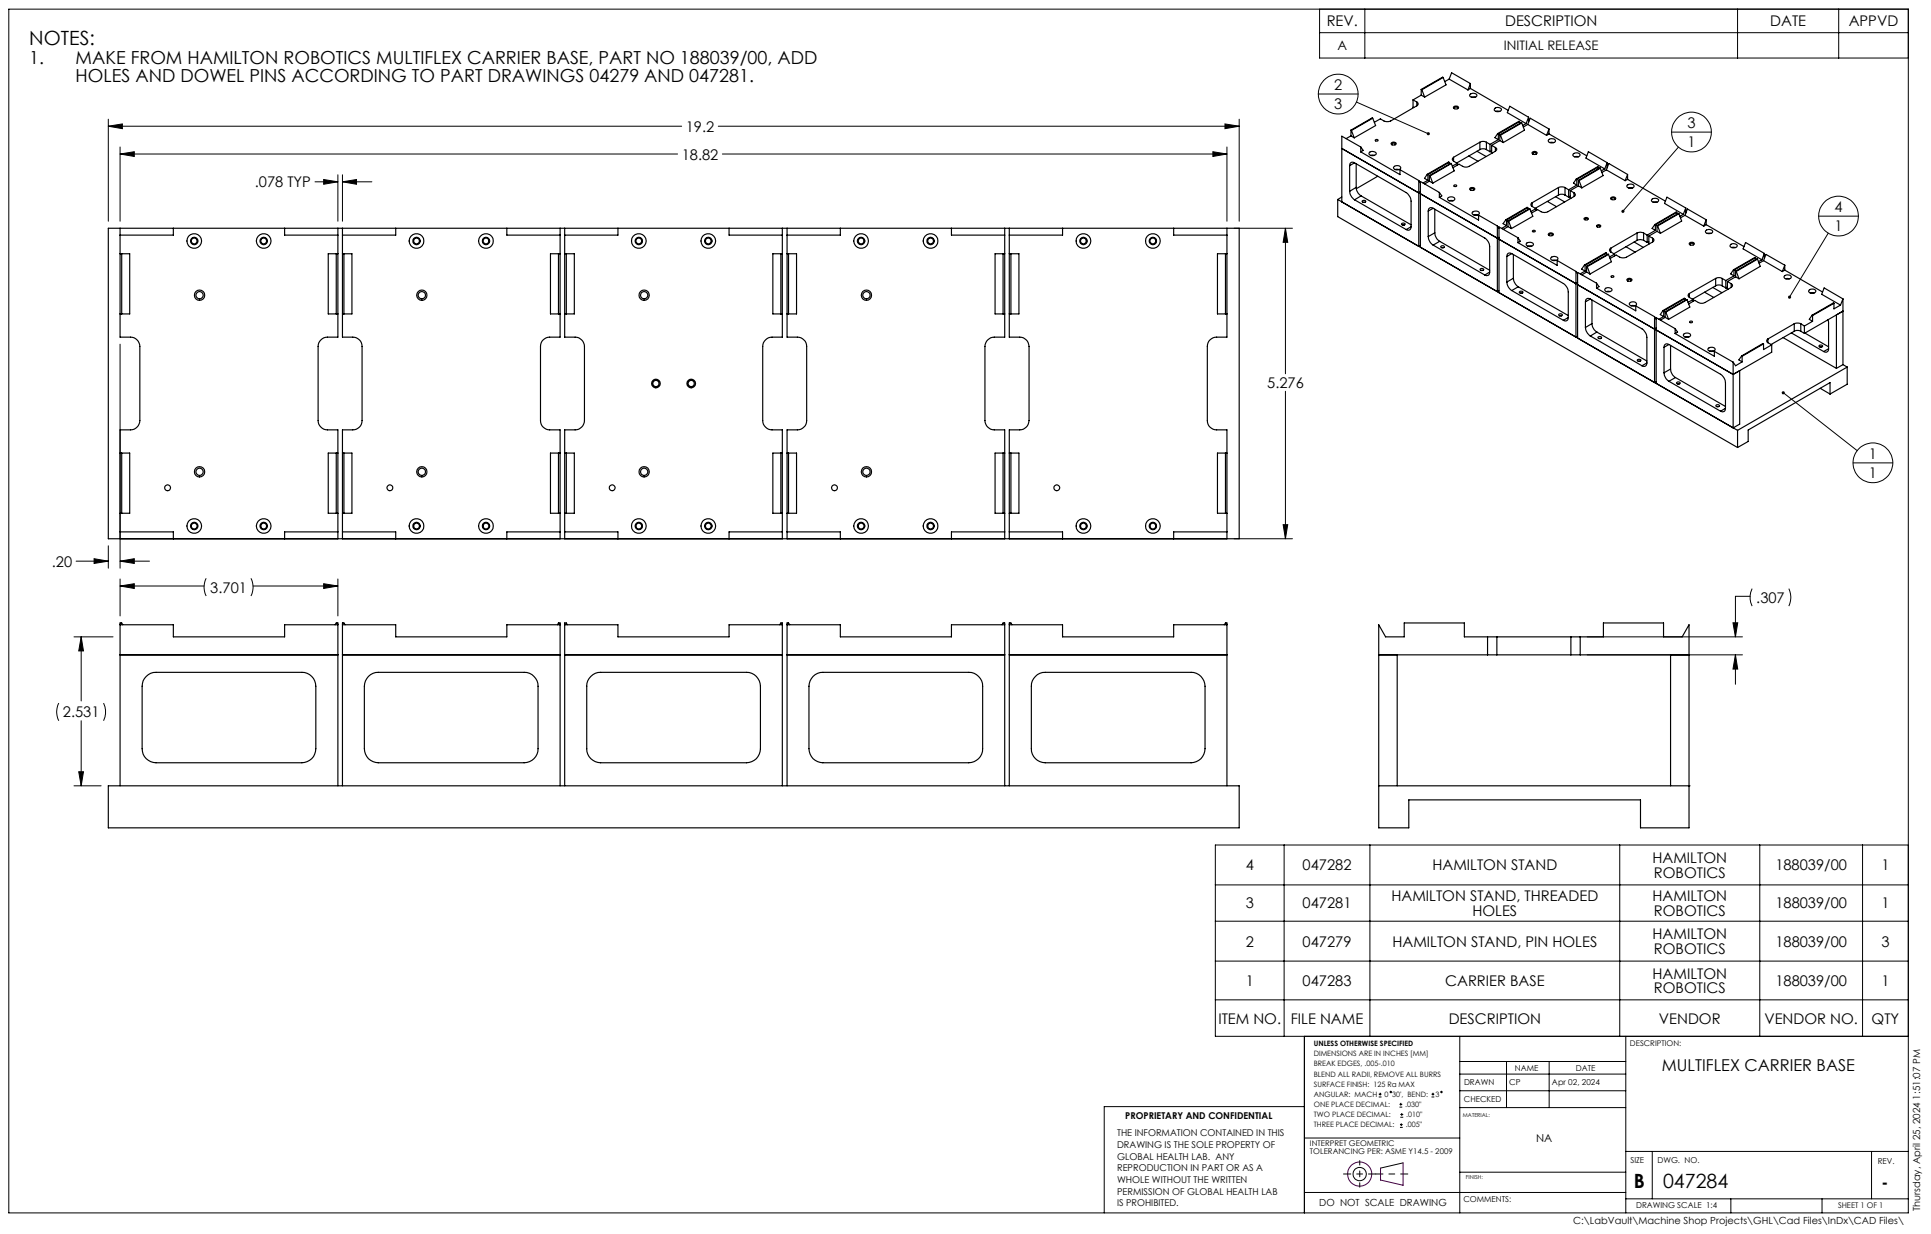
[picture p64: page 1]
.078 TYP; SHEET 1 OF 1; DO NOT SCALE DRAWING; COMMENTS:; DRAWING SCALE 1:4; DWG. NO.; Apr 02, 2024; ONE PLACE DECIMAL:; TWO PLACE DECIMAL:

REV. | DESCRIPTION | DATE | APPVD
A | INITIAL RELEASE

NOTES:
1. MAKE FROM HAMILTON ROBOTICS MULTIFLEX CARRIER BASE, PART NO 188039/00, ADD
HOLES AND DOWEL PINS ACCORDING TO PART DRAWINGS 04279 AND 047281.

4 | 047282 | HAMILTON STAND | HAMILTON ROBOTICS | 188039/00 | 1
3 | 047281 | HAMILTON STAND, THREADED HOLES | HAMILTON ROBOTICS | 188039/00 | 1
2 | 047279 | HAMILTON STAND, PIN HOLES | HAMILTON ROBOTICS | 188039/00 | 3

1 | 047283 | CARRIER BASE | HAMILTON ROBOTICS | 188039/00 | 1

ITEM NO. | FILE NAME | DESCRIPTION | VENDOR | VENDOR NO. | QTY

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

DESCRIPTION:
MULTIFLEX CARRIER BASE

Thursday, April 25, 2024 1:51:07 PM

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

C:\LabVault\Machine Shop Projects\GHL\Cad Files\InDx\CAD Files\

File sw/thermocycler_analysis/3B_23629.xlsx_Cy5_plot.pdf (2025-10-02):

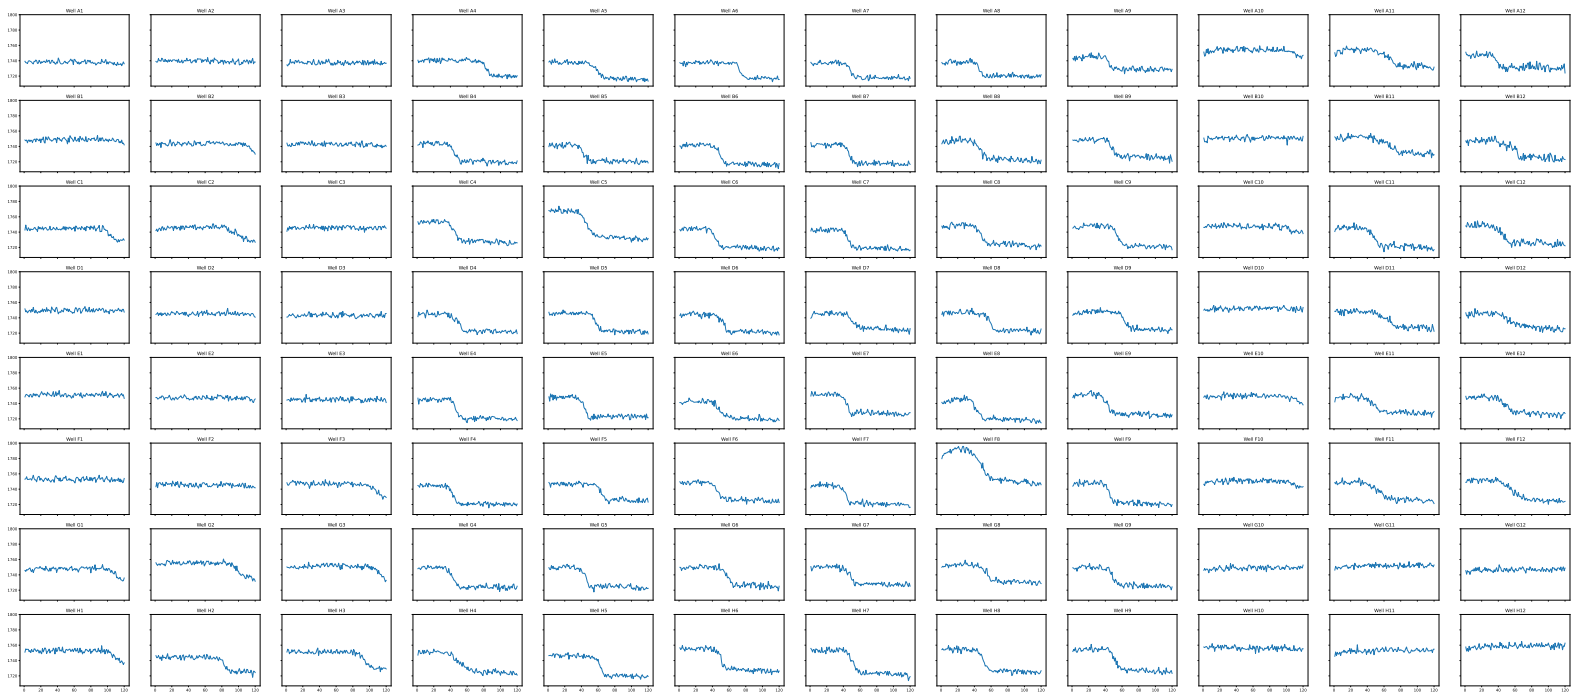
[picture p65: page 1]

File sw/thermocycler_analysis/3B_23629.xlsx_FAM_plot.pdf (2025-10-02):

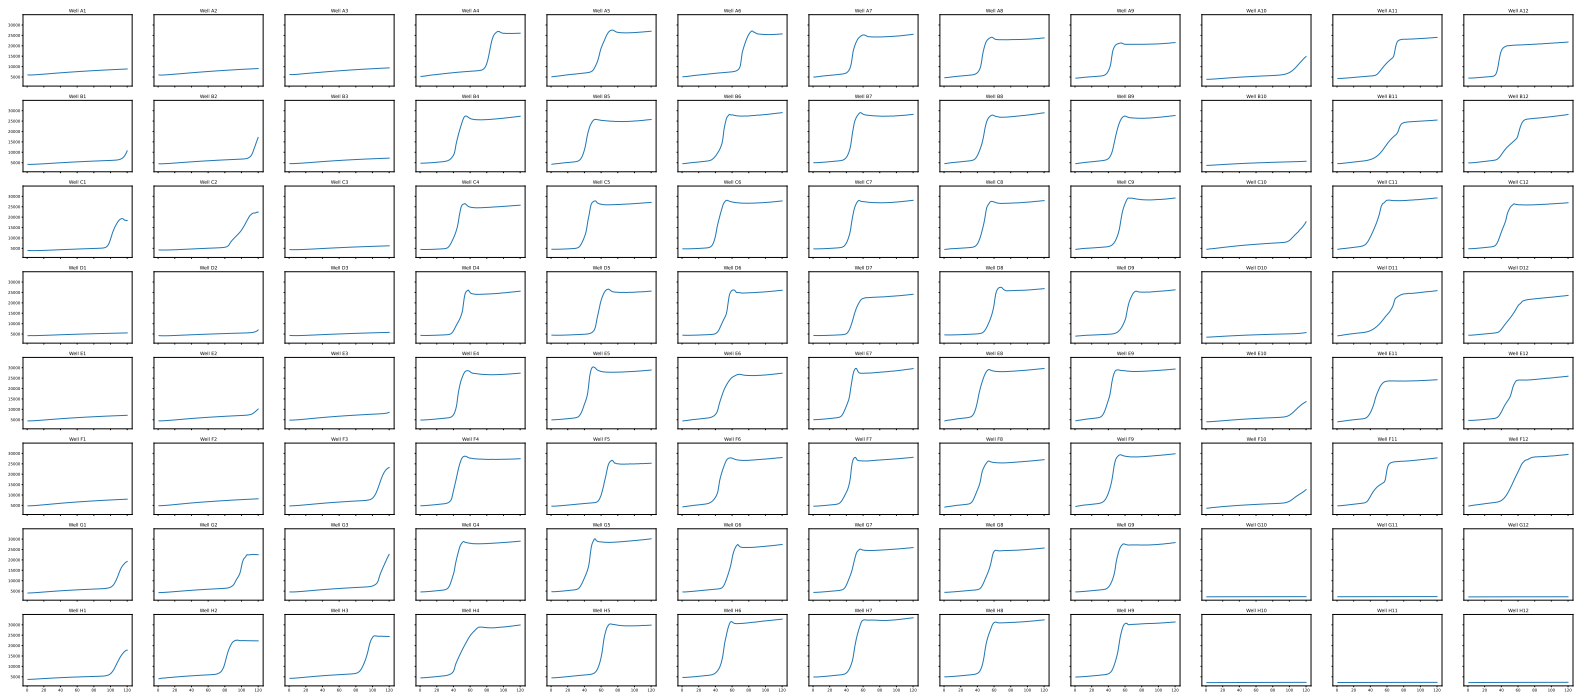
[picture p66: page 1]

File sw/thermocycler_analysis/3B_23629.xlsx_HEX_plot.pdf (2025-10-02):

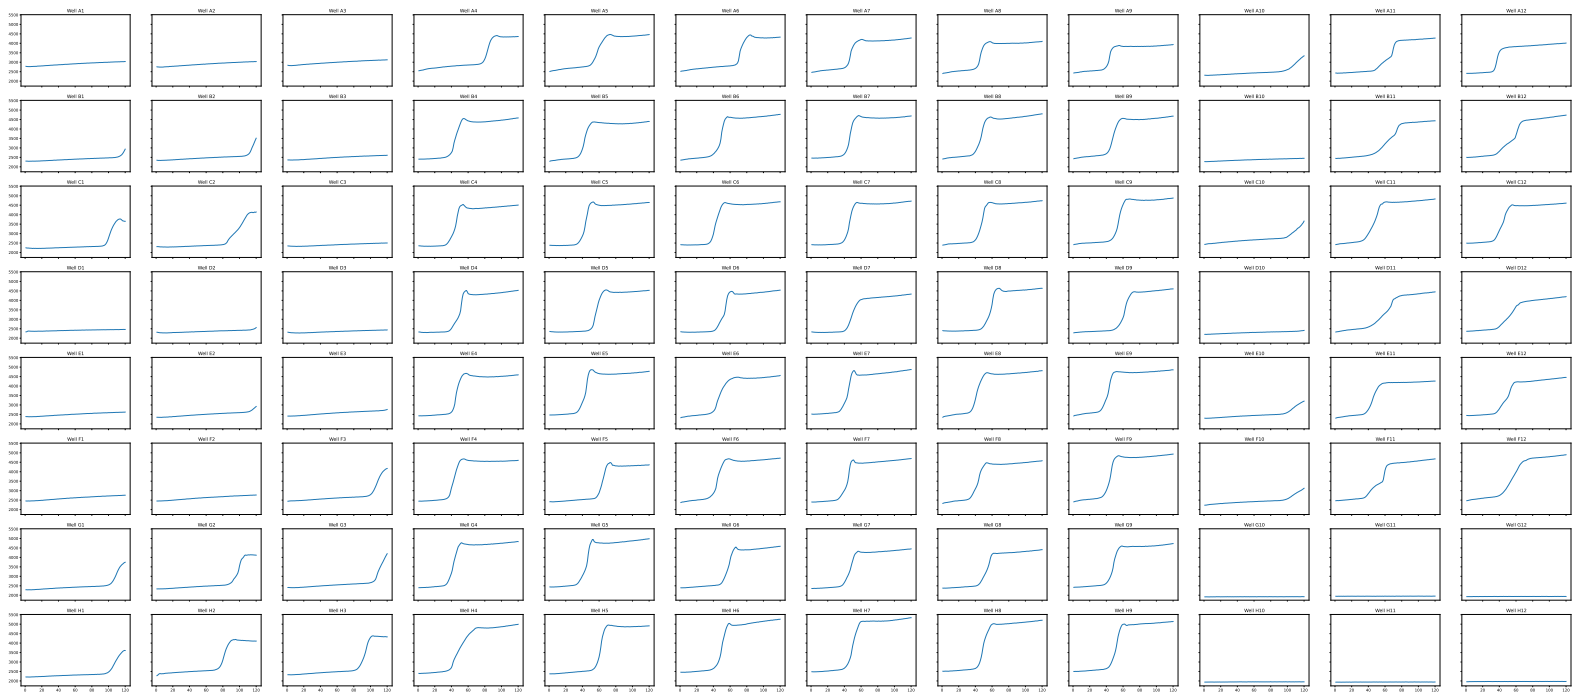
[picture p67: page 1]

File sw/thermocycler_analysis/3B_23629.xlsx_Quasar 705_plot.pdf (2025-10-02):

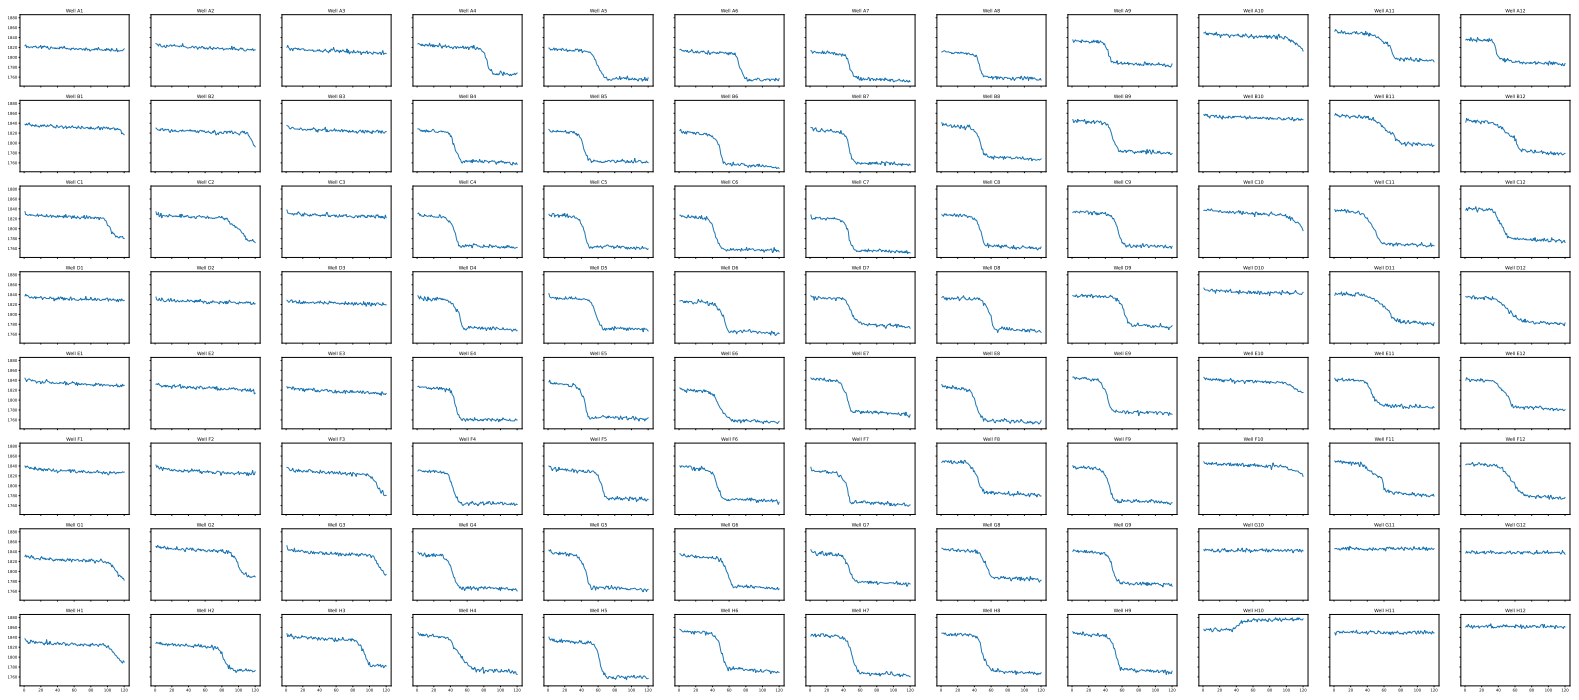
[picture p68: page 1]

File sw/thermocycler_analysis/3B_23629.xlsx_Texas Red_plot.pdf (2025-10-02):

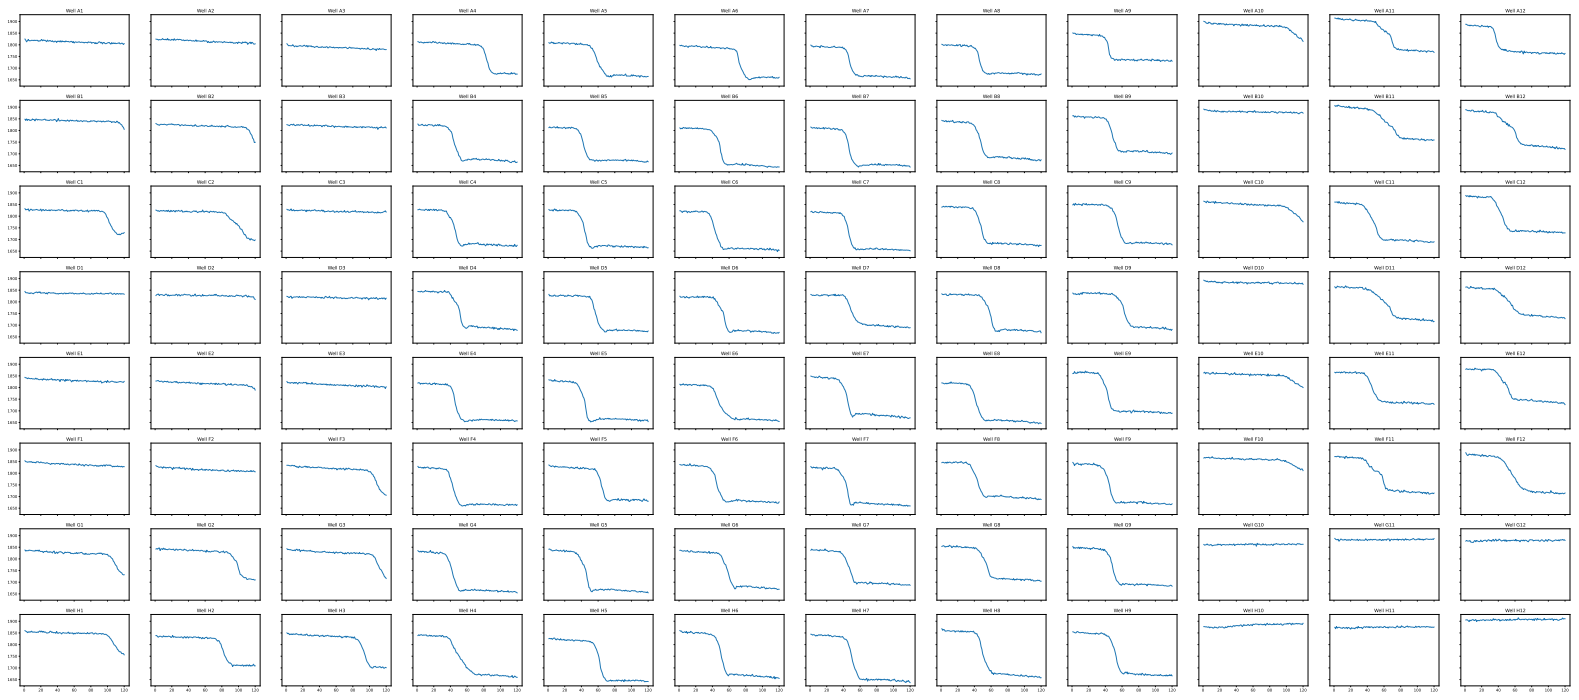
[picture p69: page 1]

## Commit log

2025-08-07 Updated content in Project Overview and Hardware pages. Fixed links in Troubleshooting Support. Added drawings and CAD files to hw folder.
    [036639.SLDDRW, 036639.sldasm, 036640.SLDDRW, 036640.sldprt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]
2025-09-19 Updated content in LFA example efforts.md.
    [5x3_full_worklist.csv]
2025-09-25 Updates to NAAT Example Efforts page
    [A1A2_makeandmix_worklist.csv, A1A2_template_aq_worklist.csv, A1A3_MM_aq_worklist.csv, A1A3_makeandmix_worklist.csv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]
2025-09-25 Updates to NAAT Example Efforts.md and related files
    [2a_makeandmix_worklist.csv, 2a_template_aq_worklist.csv, 2b_makeandmix_worklist.csv, NAAT_LOD_makeandmix_worklist.csv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]
2025-09-26 Updates to NAAT Example Efforts.md
    [2b_half_template_aq_worklist.csv, NAAT_LOD_template_aq_worklist.csv]
2025-09-29 sw folder - contents added
    [3B_23629.xlsx, 3B_23629_params.csv, 3B_23629_qoi.csv, HPV16-2 Cy5.xlsx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]
2025-09-29 Attempting failed commit
    [all_results.csv, image.csv]
2025-09-29 Fixed links for installation files
    [Test_LFA_cassette_worklist.csv, Test_LFA_strip_worklist.csv, Test_mastermix_worklist.csv, Test_sample_worklist.csv]
2025-09-30 Updates to LFA Hardware page and files
    [Hamilton_spacer.SLDPRT, Hamilton_spacer_2.SLDPRT]
2025-10-01 Added image analysis code
    [all_results.csv, image.csv]
2025-10-02 Restructured folder hierarchy
    [038379_v3.SLDPRT, 2a_makeandmix_worklist.csv, 2a_template_aq_worklist.csv, 2b_half_template_aq_worklist.csv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]
2025-10-02 Links to worklists and flowcharts updated
2025-10-02 Increased text size in LFA and NAAT flowcharts
2025-10-02 Included software modules updated with detailed Readme files.
    [3B_23629.xlsx, 3B_23629_params.csv, 3B_23629_qoi.csv, Robot vs human 384.xlsx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]
